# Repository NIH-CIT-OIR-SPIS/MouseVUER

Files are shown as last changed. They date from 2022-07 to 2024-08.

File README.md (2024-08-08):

# MouseVUER: Video based open-source system for laboratory mouse home-cage monitoring

### About

An open source home-cage design based on Intel&reg; RealSense&trade; depth cameras. 

### CAD Files and Assembly

The CAD files and assembly instructions can be found in the [CAD_Models folder](./CAD_Models/).

### Manuscript data

The images and annotations used in the manuscript can be found here [Manuscript_Data folder](./Manuscript_Data/)

# Video Acquisition Software

<p>
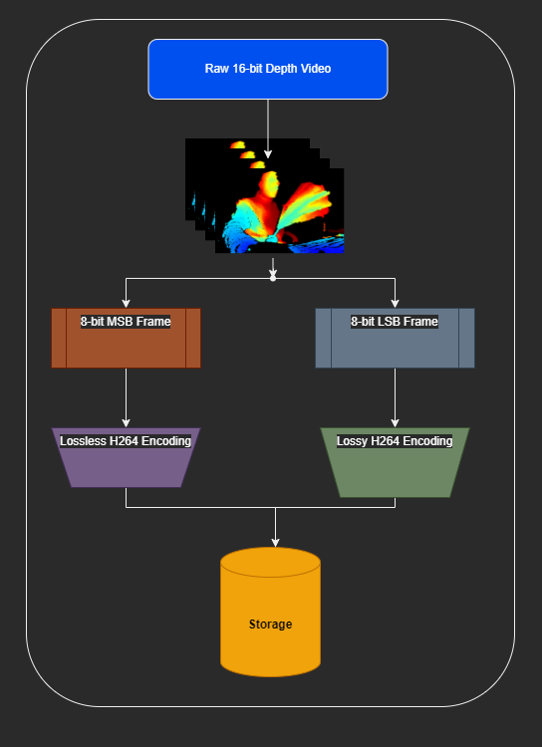
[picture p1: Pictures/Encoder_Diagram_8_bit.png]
    
    <br>
    <em>Depth Video Encoding Pipeline</em>
</p>

### Directions for Installation

### Install librealsense with Ubuntu 20.04 (as of 3/28/2023)

This is a guide on how to run the program 
To install with linux please follow directions here https://github.com/IntelRealSense/librealsense/blob/master/doc/distribution_linux.md

### Install python3 modules
```
sudo apt update && \
sudo apt install python3-pip && \
python3 -m pip install scapy && \
python3 -m pip install pycrypto && \
python3 -m pip install ffmpeg-python && \
python3 -m pip install numpy && \
sudo apt-get install python3-tk
```

### Install Boost, FFmpeg, GLFW3 and others using the following commands:

Type the following into the command line:
```
sudo apt-get -y install libboost-all-dev && \
sudo apt-get -y install libglfw3 && \
sudo apt-get -y install libglfw3-dev && \
sudo apt-get -y install freeglut3-dev libgl1-mesa-dev libglu1-mesa-dev  && \
sudo apt-get -y install libjsoncpp-dev && \
sudo apt-get -y install ffmpeg && \
sudo apt-get -y install libavcodec-dev libavutil-dev libavformat-dev libswscale-dev
```

### OPTIONAL Install Intel QuickSync
```
sudo apt install intel-media-va-driver-non-free x264 libva-dev libmfx-dev intel-media-va-driver-non-free x264 intel-media-va-driver-non-free i965-va-driver-shaders && \
export LIBVA_DRIVER_NAME=iHD
```
More info https://trac.ffmpeg.org/wiki/Hardware/VAAPI

### Install OpenCV with the following directions

https://linuxize.com/post/how-to-install-opencv-on-ubuntu-20-04/

## If the above doesn't work
from 
https://docs.opencv.org/4.6.0/d7/d9f/tutorial_linux_install.html
1) Install manually using guide below.
```
python3 -m pip install pyrealsense2 && \
sudo apt install -y g++ && \
sudo apt install -y cmake && \
sudo apt install -y make && \
sudo apt install -y wget unzip && \
sudo apt install -y git && \
cd ~/ && \
wget -O opencv.zip https://github.com/opencv/opencv/archive/4.x.zip && \
unzip opencv.zip && \
mv opencv-4.x opencv && \
mkdir -p build && cd build && \
cmake -DOPENCV_GENERATE_PKGCONFIG=ON ../opencv && \
make -j5 && \
sudo make install && \
sudo ldconfig -v
```

2) Then 

```
sudo nano /usr/local/lib/pkgconfig/opencv4.pc
```

3) And if nothing is there then copy the following to the opencv4.pc file please replace Version field with your specified version number :

```
# Package Information for pkg-config

prefix=/usr/local
exec_prefix=${prefix}
libdir=${exec_prefix}/lib
includedir=${prefix}/include/opencv4

Name: OpenCV
Description: Open Source Computer Vision Library
Version: 4.7.0 
Libs: -L${exec_prefix}/lib -lopencv_gapi -lopencv_highgui -lopencv_ml -lopencv_objdetect -lopencv_photo -lopencv_stitching -lopencv_video -lopencv_calib3d -lopencv_features2d -lopencv_dnn -lopencv_flann -lopencv_videoio -lopencv_imgcodecs -lopencv_imgproc -lopencv_core
Libs.private: -ldl -lm -lpthread -lrt
Cflags: -I${includedir}
```

4) Then do 
```
sudo nano ~/.bashrc
```

5) Now copy the following at the bottom of the .bashrc file
```
PKG_CONFIG_PATH=$PKG_CONFIG_PATH:/usr/local/lib/pkgconfig
export PKG_CONFIG_PATH
```

6) Now execute the command
```
sudo ldconfig -v
```

### Making your json file config
Connect your realsense camera and run
```
realsense-viewer
```

Then make any setting changes you wish to make and save changes using the save icon on the camera. You will be prompted to save it to a .json file
We will denote this json file as YourJsonFile.json

Save this file in the Code/ directory

### Directions for Use
Then plug in your Intel RealSense Camera into the computer's USB port

Then run:
```
cd ~/DepthCameraRecordingTool/Code/ && mkdir Testing_DIR
```

Then run:
```
make -j4
```

Or for a new run try
```
make clean && make -j4
```

Then in order to see a list of options do the following
```
./bin/multicam -h
```

### Examples
For example here is a simple recording for 30 seconds with files saved to Testing_DIR/

Decrease crf for better quality at expense of higher cpu processing and possible frame delays
thr just means number of cores you wish to utilize, default is 2, choose a number greater than 8 or 0 to cause it to use all cores
```
./bin/multicam -dir Testing_DIR/ -sec 30 -fps 30 -crf 23 -thr 0 -jsonfile Default.json
```

Record with depth, color and IR stream while aligning depth frames to color

```
./bin/multicam -dir Testing_DIR/ -sec 30 -fps 30 -crf 23 -thr 0 -jsonfile Default.json -color 1 -ir 1 -align_to_color 1
```

Record with just depth, and IR stream for 30 seconds 

```
./bin/multicam -dir Testing_DIR/ -sec 30 -fps 30 -crf 23 -thr 0 -jsonfile Default.json -ir 1
```

For command info  help type:

```
./bin/multicam -h
```

## Run multicam program

```
make -j4 && ./bin/multicam -sec 60 -thr 4 -fps 30 -crf 22 -numraw 450 -max_depth 1000 -dir Testing_DIR/ -bagfile ~/Downloads/fishy-fish.bag && ./bin/decompress Testing_DIR/test_lsb.mp4 Testing_DIR/test_msb.mp4 

```

### Decompress Lossy

Decompressing and comparing against raw files

```
./bin/decompress -ilsb Testing_DIR/test_lsb.mp4  -imsb Testing_DIR/test_msb.mp4 -hd Testing_DIR/video_head_file.txt -cmp Testing_DIR -o Testing_DIR -print_psnr 0
```

### Decompress Lossy

Decompressing regular no comparison

```
./bin/decompress -ilsb Testing_DIR/test_lsb.mp4  -imsb Testing_DIR/test_msb.mp4 -hd Testing_DIR/video_head_file.txt -o Testing_DIR -print_psnr 0
```

### Decompress each raw file seperately

```
ffmpeg -i Testing_DIR/test_lsb_5000_out.mp4 -i Testing_DIR/test_msb_5001_out.mp4 -map 0:v -c:v rawvideo -pix_fmt yuv420p Testing_DIR/output_lsb_5000.mkv -map 1:v -c:v rawvideo -pix_fmt yuv420p Testing_DIR/output_msb_5001.mkv
```

# Directions for Configuring Server Client System

### About

A server-client system for Depth Cameras.

<p>
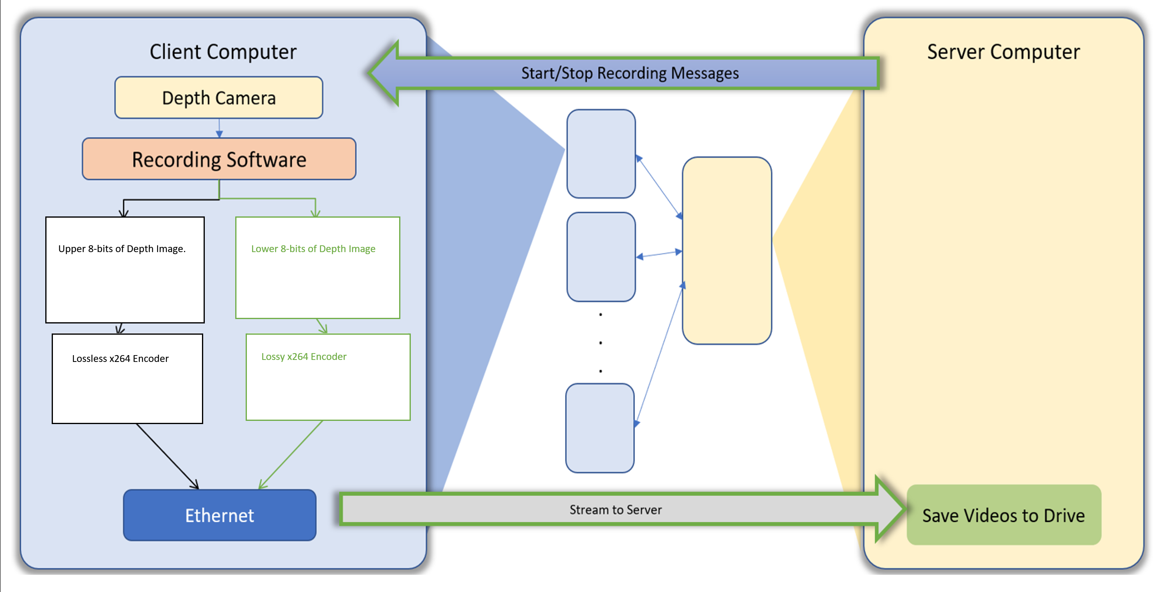
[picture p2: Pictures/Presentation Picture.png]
    
    <br>
    <em>Server-Client Configuration Diagram</em>
</p>
# Hardware Requirements.
Server computer should have more CPU cores for every client (Recommend for 3 or more systems should be at least 6th gen i5 desktop CPU or equivilant)

Client computers can be found for cheap if used (around $150 or less) for example (a used HP EliteDesk 800 G2 Mini Business Desktop with an i5-6500T is sufficiently powerful enough.)

Our configuration:
    Server (1):
        HP EliteDesk 800 G2 Mini Business Desktop with 16GB RAM and 5TB external drive
    
    Clients (multiple):
        HP EliteDesk 800 G2 Mini Business Desktop with 8GB RAM, and 128GB SSD     

Depth Cameras:
    Intel&reg; RealSense&trade; D435 Stereo Depth Cameras

Ubuntu 20.04 LTS is installed on each computer. See more configuration settings in the README.md document

## First please configure for static IP addresses:

### On server
Go to Settings -> Network -> Wired -> [Click on Settings Symbol] -> IPv4 -> Manual:

    Then enter the following into their respective boxes
    In Addresses section
        Address: 192.168.1.234
        Netmask: 255.255.255.0
        Gateway: 192.168.1.1
    In DNS section:
        8.8.4.4,8.8.8.8
    Then hit apply

**NOTE IF YOU HAVE ANY FIREWALL SETTINGS **

1) Open a terminal

2) Type in 

```
sudo ufw status verbose
```
3) You will see either an active status or inactive status

4) If you have an active status add rules so you can accept your client computer cameras

5) Type the following into a terminal 
```
sudo ufw allow proto tcp 192.168.1.201 to any port 5000 && sudo ufw allow proto tcp 192.168.1.201 to any port 5001 && \
sudo ufw allow proto tcp 192.168.1.202 to any port 5002 && sudo ufw allow proto tcp 192.168.1.202 to any port 5003 && \
sudo ufw allow proto tcp 192.168.1.203 to any port 5004 && sudo ufw allow proto tcp 192.168.1.202 to any port 5004 && \
.
.
.
...

```
If need be you can remove all the firewall rules by doing

```
sudo ufw status verbose
```

Looking at the number in the list at which the rule occurs at

```
sudo ufw delete [x] # Where x is the number in the list at which the rule occurs at which you want to delete
```
Key generation

Type the following in to a terminal on your Server

```
cd ~/DepthCameraRecordingTool/Code/ && \
make clean && make -j4 && \
python3 make_ssl_keys_cert.py
```

### On Client computers

Go to Settings -> Network -> Wired -> [Click on Settings Symbol] -> IPv4 -> Manual:
    Then enter the following into their respective boxes
    In Addresses section
        Address: 192.168.1.2xx    (Here xx means any two digit number as long as it is unique and not 34)
        Netmask: 255.255.255.0
        Gateway: 192.168.1.1
    In DNS section:
        8.8.4.4,8.8.8.8
    Then hit apply

### Copy Entire directory from Server to each client

Copy entire ~/DepthCameraRecordingTool/  directory to storage medium of your choice.
Then For ***each*** client computer:
    Navigate on the client computer to your home directory using the Files application on Ubuntu
    Paste a copy of the DepthCameraRecordingTool in this folder.

Alternativley you could just open up an ssh session to each client and copy the directories over. (This however assumes you are connecting the computers to routers)

### For each Client 
```
cd ~/DepthCameraRecordingTool/Code/ && \
make clean && \
make -j4
```

```
crontab -e
```
Then if prompted type in 1 and hit ENTER

Using the arrow keys go down to the very bottom of the file
Then add the following text replacing USER with your client username found if you go to settings and users:
```
@reboot sleep 10; export XAUTHORITY=/home/<USER>/.Xauthority; cd /home/<USER>/DepthCameraRecordingTool/Code/ && python3 client_side.py &
```
Then hit the keys CTRL+X then Y then ENTER

Then create a new bash script:
```
sudo nano /etc/NetworkManager/dispatcher.d/70-wifi-wired-exclusive.sh
```

Then copy and paste (Paste using the shortcut CTRL+SHIFT+V) the following into 70-wifi-wired-exclusive.sh:

```
#!/bin/bash
export LC_ALL=C

enable_disable_wifi ()
{
    result=$(nmcli dev | grep "ethernet" | grep -w "connected")
    if [ -n "$result" ]; then
        nmcli radio wifi off
    else
        nmcli radio wifi on
    fi
}

if [ "$2" = "up" ]; then
    enable_disable_wifi
fi

if [ "$2" = "down" ]; then
    enable_disable_wifi
fi
```
Then hit the keys CTRL+X then Y then ENTER

Then run the following command:
```
sudo chmod a+rx /etc/NetworkManager/dispatcher.d/70-wifi-wired-exclusive.sh
```

Then reboot the system
```
sudo reboot
```

Repeat for each client

## Running Server from CLI

Go to Settings -> Network -> Wired -> [Click on Settings Symbol] -> IPv4 -> Manual:
    Then enter the following into their respective boxes
    In Addresses section
        Address: 192.168.1.234
        Netmask: 255.255.255.0
        Gateway: 192.168.1.1
    In DNS section:
        8.8.4.4,8.8.8.8
    Then hit apply
    
Running a recording for 30 seconds at a crf of 22, with 4 clients connected
```
python3 server_side.py --dir Testing_DIR/ --num_clients 4 --json Default.json --time_run 30 --crf 22
```

## Running Server from GUI

Run the following command in mousePad/Code directory
```
python3 server_gui.py 
```

You should then see an image like this:

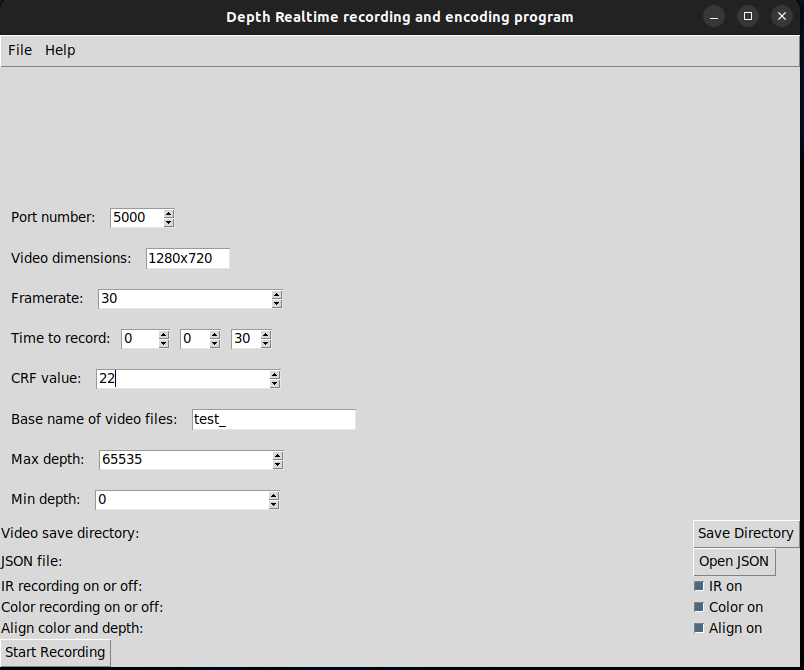
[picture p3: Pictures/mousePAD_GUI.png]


CRF values control the quality of the video. The higher the CRF value the lower the quality. Please keep it between 18-28.

Valid video dimensions are 640x480, and 1280x720

Please Choose a valid JSON to utilize.

You could also enter in your own json file as well for different settings just be sure that these files are also on the client computers.

# Directions Collecting_Training_Code/

### Running recording lossless compression with GUI

```
cd ~/DepthCameraRecordingTool/Code/Collect_Training_Code/
python3 collect_aligned_depth_training_vids.py
```

### Decompressing each frame to a TIF file GUI

```
python3 decompress_training_vids_gui.py
```

### Run collect_raw for 30 seconds using ffv1, with aligned frames from directory Collect_Training_Code/

make -j4 && ./bin/collect_raw -dir Testing_DIR/ -sec 30 -align 1 -jsonfile ../Code/Default.json

# Other Helpful Commands for Developers
To look at frame rates

```
ffprobe Testing_DIR/test_lossy.h265 -count_frames -show_entries stream=nb_read_frames,avg_frame_rate,r_frame_rate
```

To look at stats of a video please see the following from (https://ffmpeg.org/ffprobe-all.html)

```
ffprobe -f lavfi movie=Testing_DIR/test_lsb.mp4,signalstats -show_entries frame_tags=lavfi.signalstats.YMAX,lavfi.signalstats.YMIN,lavfi.signalstats.YAVG,lavfi.signalstats.YBITDEPTH,lavfi.signalstats.YDIF
```
Automate GDB

```
for i in {1..20}; do gdb -q -ex 'set pagination off' -ex 'set args -dir Testing_DIR/ -sec 15 -numraw 450 -crf 17 -bagfile ~/Downloads/One_Mouse_5_minutes_depth.bag' -ex run  ./bin/multicam -ex quit; done
```

Play videos side by side ffplay

```
ffplay -f lavfi "movie=left.mp4,scale=iw/2:ih[v0];movie=right.mp4,scale=iw/2:ih[v1];[v0][v1]hstack"
```

See info ffmpeg
```
ffmpeg -h encoder=libx264
```

## Utility Functions found in ~/DepthCameraRecordingTool/Code/util_functions
```
python3 decompress_from_bag_file.py -f test.bag -o Testing_DIR/
```

From depth coordinates (feeding in depth frame as png or tif) to xyz world coordinates given a set of points on the image plane in this example I am using 3 coordinates, you can use any number of coordinates, 
```
python3 from_depth_to_xyz.py -cal ../Testing_DIR/intrinsics.json -d Testing_DIR2/depth/depth_frm_40.tif -l "(13,20),(13,30),(640, 360)"
```

```
python3 script_sort_depth.py -f /media/<username>/DRIVE/images -f2 /media/<username>/DRIVE/out\(Gouda\)/
```

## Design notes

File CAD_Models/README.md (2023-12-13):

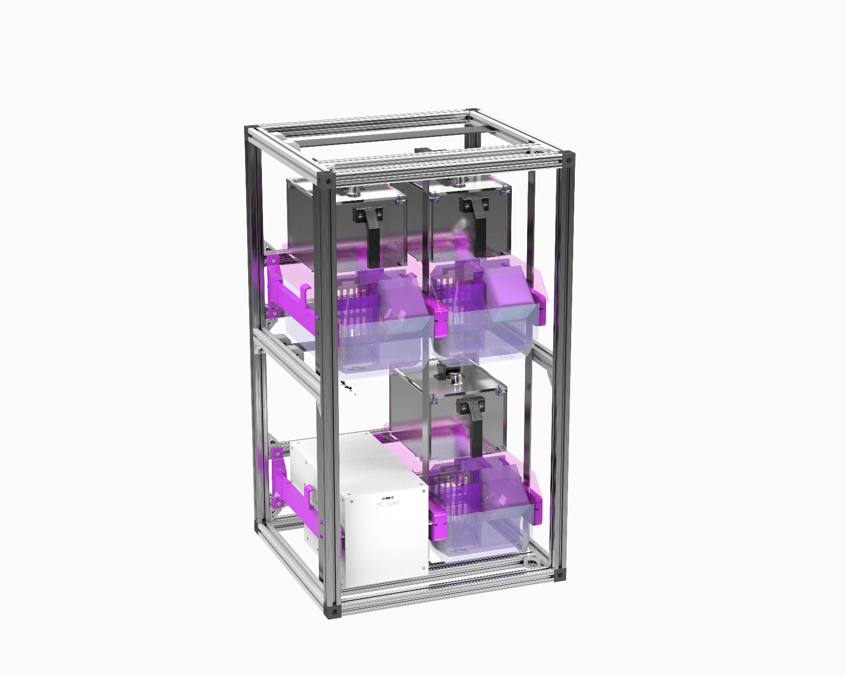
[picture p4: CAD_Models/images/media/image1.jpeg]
{width="4.468751093613299in"
height="6.0in"}

# Table of Contents {#table-of-contents .TOC-Heading}

[MouseVUER System Overview
[4](#mousevuer-system-overview)](#mousevuer-system-overview)

[The Monitoring Cage Assembly
[4](#the-monitoring-cage-assembly)](#the-monitoring-cage-assembly)

[The Monitoring Cage Overview
[4](#the-monitoring-cage-overview)](#the-monitoring-cage-overview)

[Monitoring Cage Unit Fabrication
[5](#monitoring-cage-unit-fabrication)](#monitoring-cage-unit-fabrication)

[Modified Lid Fabrication
[5](#modified-lid-fabrication)](#modified-lid-fabrication)

[Hopper Fabrication [5](#hopper-fabrication)](#hopper-fabrication)

[Camera Mounting Enclosure Fabrication [5](#camera-mounting-enclosure-fabrication)](#camera-mounting-enclosure-fabrication)

[Monitoring Cage Assembly
[6](#monitoring-cage-assembly)](#monitoring-cage-assembly)

[Hopper Assembly [7](#hopper-assembly)](#hopper-assembly)

[Camera Mounting Enclosure Assembly [8](#camera-mounting-enclosure-assembly)](#camera-mounting-enclosure-assembly)

[Finished Monitoring Cage Unit Assembly
[10](#finished-monitoring-cage-unit-assembly)](#finished-monitoring-cage-unit-assembly)

[The Power and Control Module (PCM) Assembly
[12](#the-power-and-control-module-pcm-assembly)](#the-power-and-control-module-pcm-assembly)

[PCM Overview [12](#pcm-overview)](#pcm-overview)

[System Fabrication [12](#system-fabrication)](#system-fabrication)

[Enclosure Fabrication
[13](#enclosure-fabrication)](#enclosure-fabrication)

[The PCM Assembly [13](#the-pcm-assembly)](#the-pcm-assembly)

[Side and Top Panel Assemblies
[16](#side-and-top-panel-assemblies)](#side-and-top-panel-assemblies)

[Electronic Subassemblies
[17](#electronic-subassemblies)](#electronic-subassemblies)

[Main Body Assembly [19](#main-body-assembly)](#main-body-assembly)

[Modular Rack Assembly
[23](#modular-rack-assembly)](#modular-rack-assembly)

[Modular Rack Overview
[23](#modular-rack-overview)](#modular-rack-overview)

[Modular Rack Fabrication
[23](#modular-rack-fabrication)](#modular-rack-fabrication)

[Modular Rack Assembly
[23](#modular-rack-assembly-1)](#modular-rack-assembly-1)

[Appendix -- Step by Step Instructions
[35](#appendix-step-by-step-instructions)](#appendix-step-by-step-instructions)

[Monitoring Cage Assembly
[35](#monitoring-cage-assembly-1)](#monitoring-cage-assembly-1)

[Hopper Assembly [35](#hopper-assembly-1)](#hopper-assembly-1)

[Camera Mounting Enclosure Assembly [37](#camera-mounting-enclosure-assembly-1)](#cme-assembly-1)

[Monitoring Cage Unit Assembly
[42](#monitoring-cage-unit-assembly)](#monitoring-cage-unit-assembly)

[Power and Control Module (PCM)
[44](#power-and-control-module-pcm)](#power-and-control-module-pcm)

[Side Panel Subassembly [44](#_Toc147213275)](#_Toc147213275)

[Top Panel Subassembly
[48](#top-panel-subassembly)](#top-panel-subassembly)

[Power Supply Subassembly
[49](#power-supply-subassembly)](#power-supply-subassembly)

[Power Distribution Board Subassembly
[50](#power-distribution-board-subassembly)](#power-distribution-board-subassembly)

[SBC Subassembly [51](#sbc-subassembly)](#sbc-subassembly)

[PCM Main Body Assembly
[53](#pcm-main-body-assembly)](#pcm-main-body-assembly)

[Modular Rack Assembly
[65](#modular-rack-assembly-2)](#modular-rack-assembly-2)

[Rack Top Subassembly
[65](#rack-top-subassembly-1)](#rack-top-subassembly-1)

[Rack Base Subassembly
[70](#rack-base-subassembly-1)](#rack-base-subassembly-1)

[Rack Mid Bar Subassembly
[74](#rack-mid-bar-subassembly-1)](#rack-mid-bar-subassembly-1)

[Rack Rear Bar Subassembly
[76](#rack-rear-bar-subassembly-1)](#rack-rear-bar-subassembly-1)

[Rack Assembly [78](#rack-assembly-1)](#rack-assembly-1)

# 

# MouseVUER System Overview

The Mouse Video Utility for Experiments Recording (MouseVUER) is an
open-source system for housing and monitoring rodents for experiments.
The MouseVUER system fits inside a custom modular rack that houses all
the components for running the system. The monitoring cage units are
where the rodents are monitored. There are three monitoring cage units
per MouseVUER system. Each monitoring unit has subassemblies including
a Camera Mounting Enclosure and Hopper that must be assembled. The camera mounting enclosure supports the
camera and LEDs above the mouse lid. The hopper is specially designed to
fit into the mouse cages and supply food and water. One Power and
Control Module (PCM) will need to be fabricated for every MouseVUER
system. The PCM is responsible for powering and housing electronics to
run the MouseVUER system. Figure 1 shows the components of the MouseVUER
system.

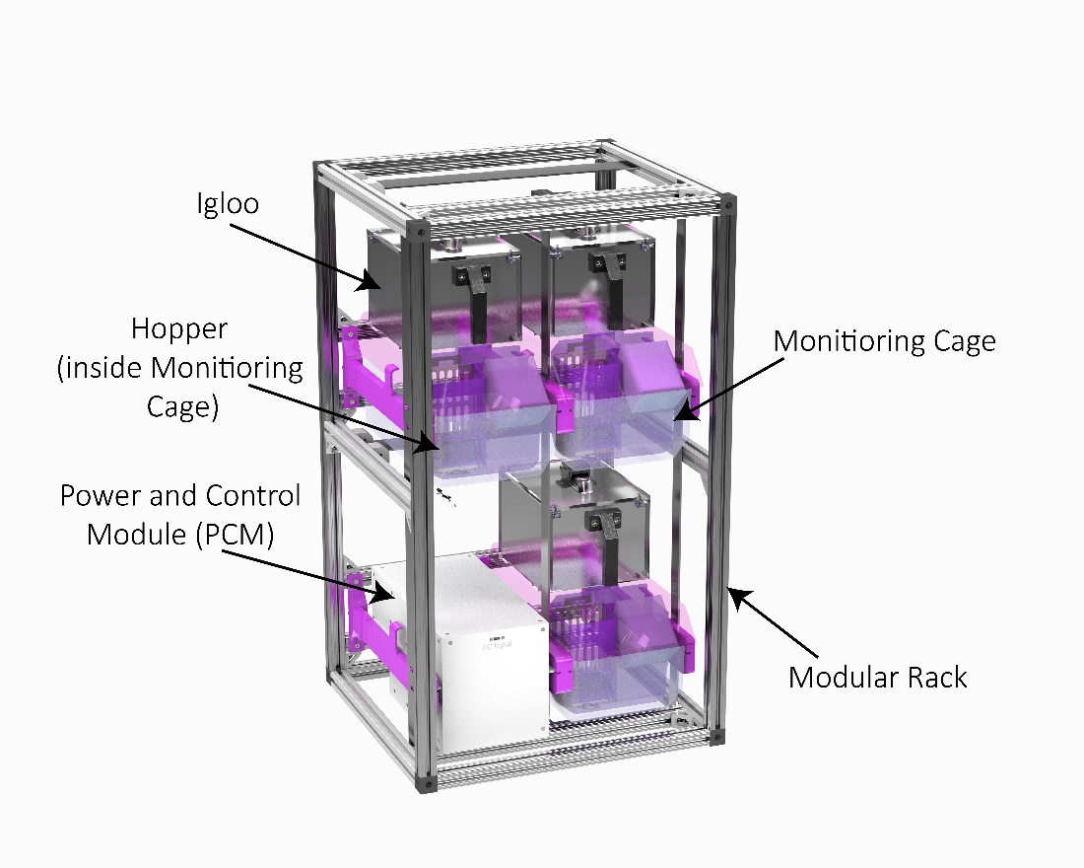
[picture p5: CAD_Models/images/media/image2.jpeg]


Figure 1 Fully assembled MouseVUER system.

This document is organized into subassemblies to build the final
MouseVUER system. Each subassembly has a fabrication and assembly
section. Each subassembly has a bill of materials for one subassembly
unit. In the appendix, larger figures of all assembly steps are shown.

# The Monitoring Cage Assembly

## The Monitoring Cage Overview

The Monitoring Cage units are where the rodents are monitored. These
instructions are for one Monitoring Cage unit and must be repeated two
more times for each MouseVUER system. The Monitoring Cage unit has
subassemblies called the Camera Mounting Enclosure and Hopper that must be assembled before
assembling the final Monitoring Cage unit.

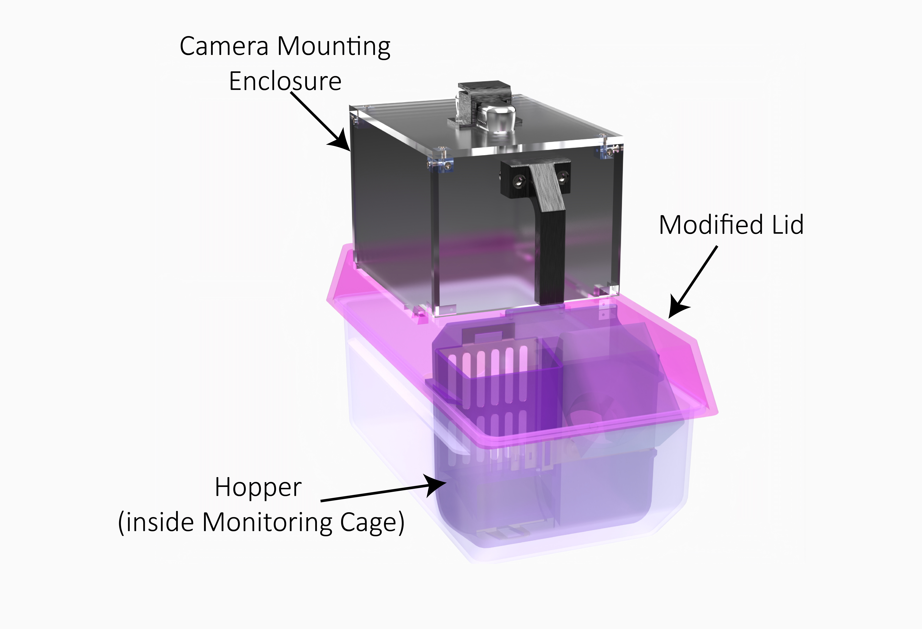
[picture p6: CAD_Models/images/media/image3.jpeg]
{width="5.865580708661417in"
height="4.0in"}

Figure 2 The final Monitoring Cage unit Assembly

## Monitoring Cage Unit Fabrication

### Modified Lid Fabrication

A solid clear NexGen lid (P/N: 228790-1, Allentown Inc, Allentown, NJ)
will need to be modified to support the Monitoring Cage unit. A DXF file
can be found on the Github page, and it will need to cut into the lid.
In this fabrication process, a waterjet was used to make the cuts into
the lid. In this process, a single pass of the waterjet was used even
for the varying heights of the lid.

### Hopper Fabrication

The two-compartment hopper was designed to house food pellets and a
water bottle inside the NexGen standard cage (P/N: 223581-4, Allentown
Inc, Allentown, NJ). The hopper must be injection molded (ICOMold Inc.,
Hartland, WI) from a food safe, autoclavable material (PSU Ultrason
S3010, BASF, Ludwigshafen, Germany). The food grate (304SS, 26-gauge,
Yarde Metal, White Marsh, MD) is fabricated with a waterjet and bending
tool. The bottle holder (304SS, 24-gauge, Yarde Metal, White Marsh, MD)
is fabricated with a waterjet.

### Camera Mounting Enclosure Fabrication

The camera mounting enclosure consists of five clear acrylic panels fixed together to
support a camera above the mouse cage. The acrylic panels (Clear Cast
Acrylic-1/4", Piedmont Plastics, Elkridge, Maryland) must be cut. In
this fabrication process a CO~2~ laser cutter (PLS6.150D, Universal
Laser Systems) was used for cutting the panels. Holes on the panels will
need to be countersink with a 90° Countersink drill bit. Two holes on
the top panel will need to be tapped for 4-40 threads. The handle and
camera bracket will need to be 3D printed. In this fabrication process,
the Markforged X7 (Waltham, MA) was used to print the parts out of Onyx.

## Monitoring Cage Assembly

The bill of materials for the assembly of one Monitoring Cage unit is
shown in Table 1. The mouse cage lid must be modified before assembling
the Monitiroing Cage unit. Items that were custom made have .STP or .DXF
or .STL files to reference on the Github page. All other items were
purchased from vendors.

<table>
<caption><p>Bill of materials for the assembly of one MouseVUER
unit.</p></caption>
<colgroup>
<col style="width: 7%" />
<col style="width: 15%" />
<col style="width: 22%" />
<col style="width: 14%" />
<col style="width: 17%" />
<col style="width: 8%" />
<col style="width: 14%" />
</colgroup>
<tbody>
<tr class="odd">
<td>ITEM NO.</td>
<td>Part Label</td>
<td>Description</td>
<td>Source</td>
<td>Vendor Part Number</td>
<td>Qty</td>
<td>Cost</td>
</tr>
<tr class="even">
<td>1</td>
<td>Mouse Cage Base</td>
<td>MOUSE, XJ/NEXGEN, CLEAR POLYSULFONE HIGH TEMPERATURE PLASTIC, WHITE
AIR KUP</td>
<td>Allentown Inc.</td>
<td>223581-4</td>
<td>1</td>
<td>$48.60</td>
</tr>
<tr class="odd">
<td>2</td>
<td>Mouse Cage Lid</td>
<td>MICRO BARRIER TOP, MOUSE, NEXGEN, SOLID, CLEAR POLYSULFONE HIGH
TEMPERATURE PLASTIC, NO LOCKS</td>
<td>Allentown Inc.</td>
<td>228790-1</td>
<td>1</td>
<td>$139.50</td>
</tr>
<tr class="even">
<td>3</td>
<td>Water bottle</td>
<td> Bottle Udel 9 oz., Ink with "O" Ring</td>
<td>Thoren Caging Systems, Inc.</td>
<td>BW09UIRNO</td>
<td>1</td>
<td>$7.11</td>
</tr>
<tr class="odd">
<td>4</td>
<td>Sipper Tube</td>
<td>Stainless steel with 2 1/2" welded bent sipper tube</td>
<td>Thoren Caging Systems, Inc.</td>
<td>BWCS250HSB</td>
<td>1</td>
<td>$3.79</td>
</tr>
<tr class="even">
<td>5</td>
<td>Hopper</td>
<td>PSU Ultrason S3010</td>
<td>Injection Molded</td>
<td>N/A - refer to STP file</td>
<td>1</td>
<td>$92.19</td>
</tr>
<tr class="odd">
<td>6</td>
<td>Stainless Steel Grommet</td>
<td>Stainless Steel Fabric Grommets with Washer</td>
<td>McMaster-Carr</td>
<td>96015K33</td>
<td>1</td>
<td>$16.68</td>
</tr>
<tr class="even">
<td>7</td>
<td>Food Grate</td>
<td>304SS, 26 Gauge stock piece</td>
<td>Waterjet Cut</td>
<td>N/A - refer to DXF file</td>
<td>1</td>
<td></td>
</tr>
<tr class="odd">
<td>8</td>
<td>Bottle Holder</td>
<td>304SS, 24 Gauge stock piece</td>
<td>Waterjet Cut</td>
<td>N/A - refer to DXF file</td>
<td>1</td>
<td></td>
</tr>
<tr class="even">
<td>9</td>
<td>4-40, 3/8" Flat</td>
<td>Passivated 18-8 Stainless Steel Phillips Flat Head Screw</td>
<td>McMaster-Carr</td>
<td>91099A165</td>
<td>2</td>
<td>$5.55</td>
</tr>
<tr class="odd">
<td>10</td>
<td>Camera</td>
<td>Depth Camera D435</td>
<td>Intel Inc.</td>
<td>D435</td>
<td>1</td>
<td>$314.00</td>
</tr>
<tr class="even">
<td>11</td>
<td>Camera Bracket</td>
<td>3D Printed FDM</td>
<td>3D printed</td>
<td>N/A - refer to STL file</td>
<td>1</td>
<td>$3.00</td>
</tr>
<tr class="odd">
<td>12</td>
<td>1/4"-20, 3/8" Flat</td>
<td>Passivated 18-8 Stainless Steel Phillips Flat Head Screw</td>
<td>McMaster-Carr</td>
<td>91771A535</td>
<td>1</td>
<td>$12.13</td>
</tr>
<tr class="even">
<td>13</td>
<td>1/4"-20 Nut</td>
<td>18-8 Stainless Steel Thin Hex Nut</td>
<td>McMaster-Carr</td>
<td>91847A029</td>
<td>2</td>
<td>$6.36</td>
</tr>
<tr class="odd">
<td>14</td>
<td>1/4"-20, 7/8" Flat</td>
<td>Passivated 18-8 Stainless Steel Phillips Flat Head Screw</td>
<td>McMaster-Carr</td>
<td>91099A478</td>
<td>2</td>
<td>$12.99</td>
</tr>
<tr class="even">
<td>15</td>
<td>Handle</td>
<td>3D Printed FDM</td>
<td>3D printed</td>
<td>N/A - refer to STL file</td>
<td>1</td>
<td>$10.00</td>
</tr>
<tr class="odd">
<td>16</td>
<td>M3, 10mm Flat</td>
<td>316 Stainless Steel Phillips Flat Head Screw</td>
<td>McMaster-Carr</td>
<td>91801A156</td>
<td>12</td>
<td>$9.91</td>
</tr>
<tr class="even">
<td>17</td>
<td>Camera Mounting Enclosure Front Panel</td>
<td>Cut from 12"x24"x1/4" Clear Cast Acrylic</td>
<td>Laser Cut</td>
<td>N/A - refer to DXF file</td>
<td>1</td>
<td>$13.00</td>
</tr>
<tr class="odd">
<td>18</td>
<td>Camera Mounting Enclosure Side Panel</td>
<td>Cut from 12"x24"x1/4" Clear Cast Acrylic</td>
<td>Laser Cut</td>
<td>N/A - refer to DXF file</td>
<td>2</td>
<td>$13.00</td>
</tr>
<tr class="even">
<td>19</td>
<td>Camera Mounting Enclosure Top Panel</td>
<td>Cut from 12"x24"x1/4" Clear Cast Acrylic</td>
<td>Laser Cut</td>
<td>N/A - refer to DXF file</td>
<td>1</td>
<td>$13.00</td>
</tr>
<tr class="odd">
<td>20</td>
<td>Cube Standoff</td>
<td>Aluminum M3 Modding Cubes</td>
<td>V1 Tech</td>
<td>N/A</td>
<td>4</td>
<td>$5.00</td>
</tr>
<tr class="even">
<td colspan="6">Total Cost Per MouseVUER Unit</td>
<td>$725.81</td>
</tr>
</tbody>
</table>

### Hopper Assembly 

The hopper subassembly should be completed before inserting into the
Monitoring Cage unit. The first step involves using a hammer-driven
punch (9612K28, McMaster-Carr, Elmhurst, IL) to lock the stainless steel
grommet in place. The food grate is then inserted and locked in by two
tabs. Lastly, the bottle holder is inserted and locked in via tabs. The
hopper assembly instructions are shown in Figure 3.

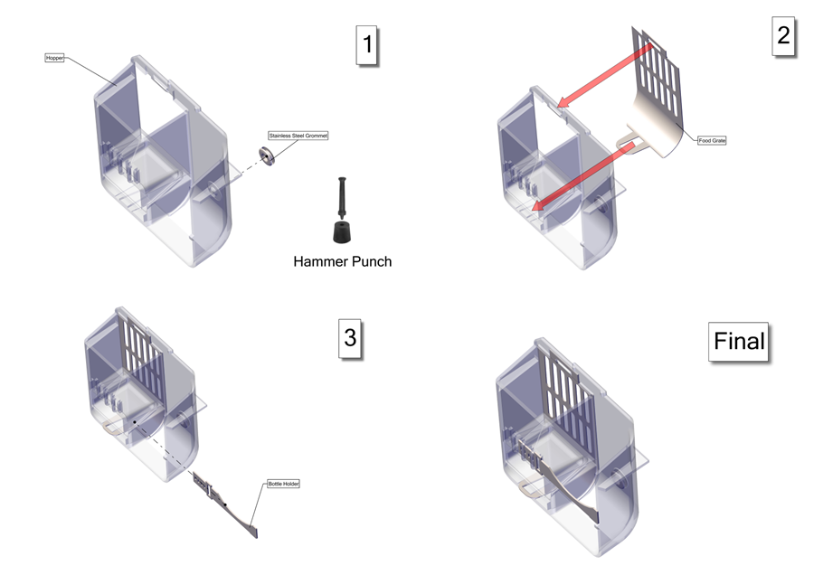
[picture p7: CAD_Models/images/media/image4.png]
{width="6.000694444444444in"
height="4.240277777777778in"}

Figure 3 The Hopper sub assembly.

### Camera Mounting Enclosure Assembly 

The Camera Mounting Enclosure subassembly must be completed before inserting into the
Monitoring Cage unit. A Phillips no. 2 screwdriver will be required for
fastening all screws in this section. The first four steps in the Camera Mounting Enclosure
assembly are shown in Figure 4. Four cube standoffs will be fastened to
the top panel with four M3, 10mm flat screws. The rear panel will be
secured via two M3, 10mm flat screws. Next, the 2 side panels will be
secured by two M3, 10mm flat screws for each panel.

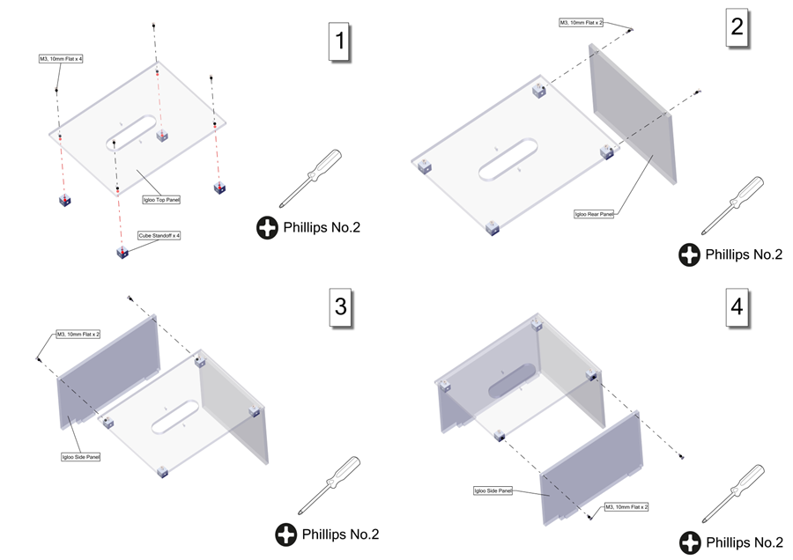
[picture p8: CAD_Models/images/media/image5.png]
{width="5.660661636045495in"
height="4.0in"}

Figure 4 Steps 1 to 4 of the Camera Mounting Enclosure subassembly.

The next step is to fasten the front panel with two M3, 10mm flat
screws. The handle will be secured in place via two ¼"-20, 7/8" flat
screws and two ¼"-20 nuts. The camera is bolted to the camera bracket by
a ¼"-20, 3/8" flat screw. Two 4-40, 3/8" screws are used to fasten the
camera bracket to the Camera Mounting Enclosure. These steps are shown in Figure 5. The
final Camera Mounting Enclosure subassembly is shown in Figure 6.

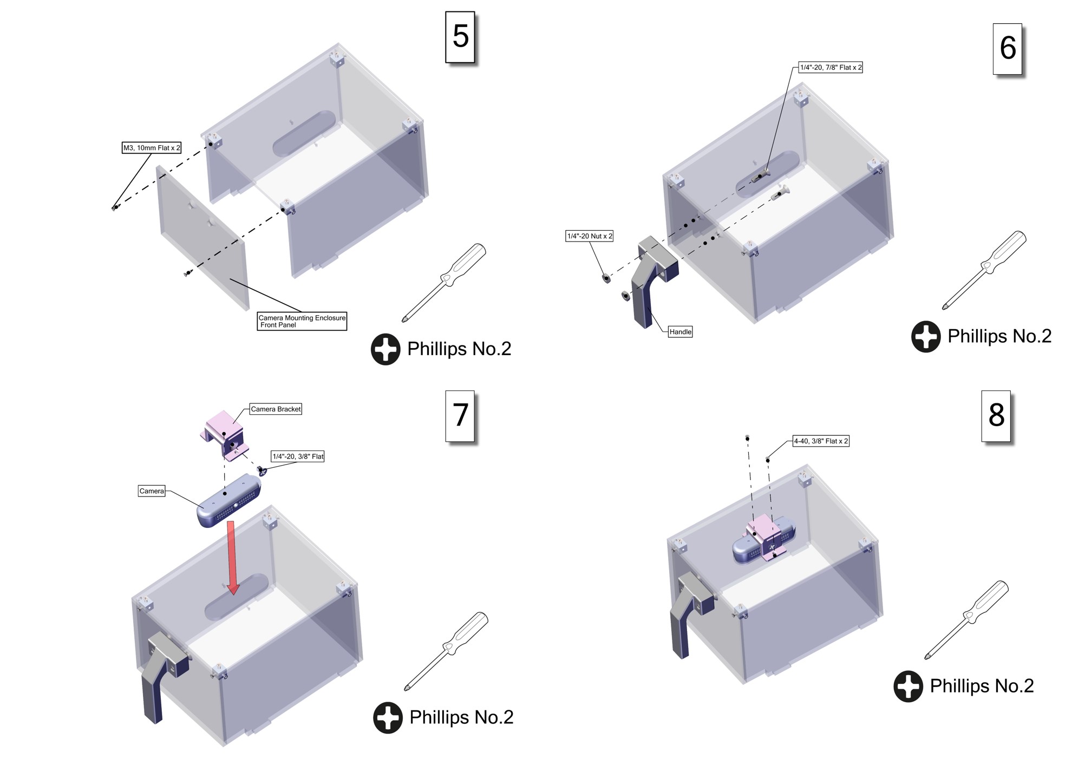
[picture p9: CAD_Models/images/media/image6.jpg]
{width="5.660661636045495in"
height="4.0in"}

Figure 5 Steps 5 to 8 for the Camera Mounting Enclosure subassembly.

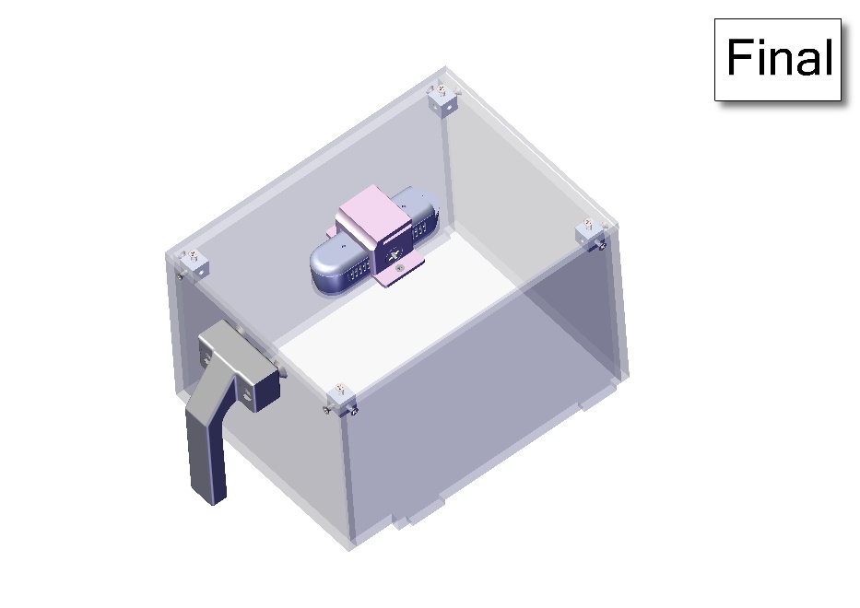
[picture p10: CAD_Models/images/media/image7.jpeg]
{width="4.24297353455818in"
height="3.0in"}

Figure 6 The final Camera Mounting Enclosure subassembly.

### Finished Monitoring Cage Unit Assembly 

Once the hopper and camera mounting enclosure assemblies are completed, the Monitoring Cage
unit can be constructed. Four steps are required in this process, and
they are shown in Figure 7. The first step is to insert the hopper near
the front of the mouse cage base. Next, the water bottle is inserted
into the hopper. The third step involves securing the hopper in place
via a tab on the mouse cage lid. The blue arrow in step 3 shows the
locking tab. The last step is to insert the camera mounting enclosure to the mouse cage lid
by aligning the four cutouts shown via 4 red arrows. The final
Monitoring Cage assembly is shown in Figure 8.

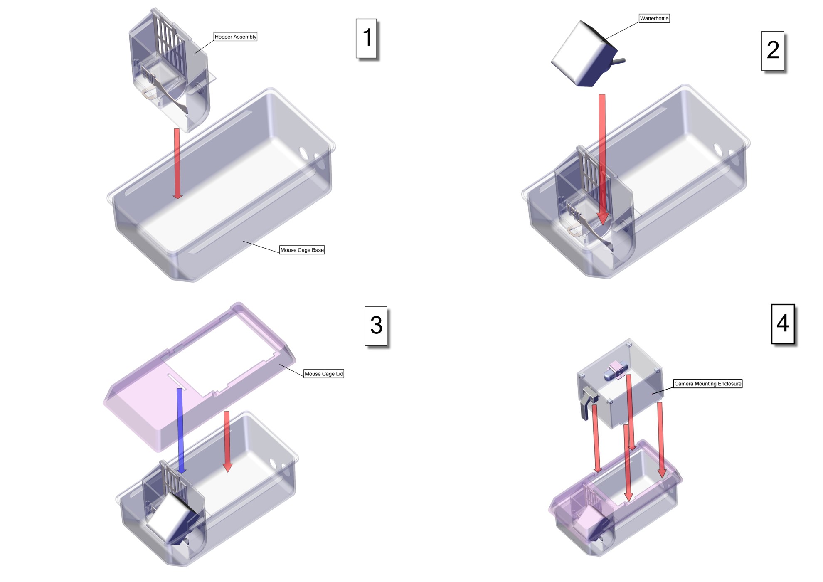
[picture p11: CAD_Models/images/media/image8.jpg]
{width="5.660661636045495in"
height="4.0in"}

Figure 7 The steps to complete the Monitoring Cage assembly.

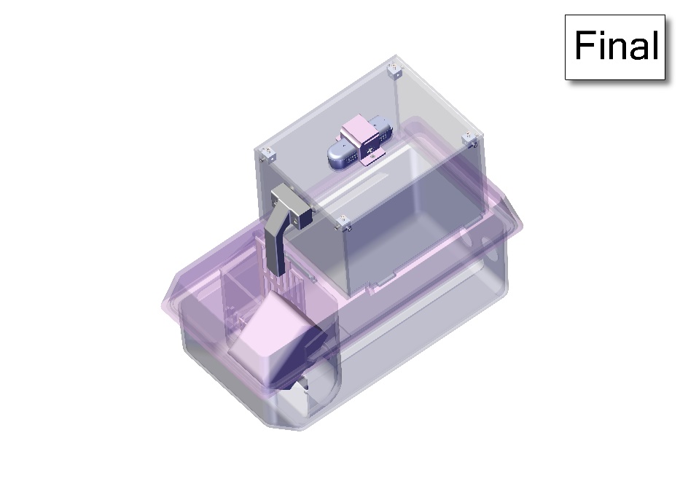
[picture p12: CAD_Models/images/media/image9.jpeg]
{width="4.24297353455818in"
height="3.0in"}

Figure 8 The final Monitoring Cage assembly.

# The Power and Control Module (PCM) Assembly

## PCM Overview

The PCM is responsible for powering, controlling, and data communication
with three Monitoring Cage units to successfully monitor the rodents.
The PCM is designed to slide into one of the open slots on the custom
racks using 3D printed rails. The PCM will have electronic connections
in the rear to the three Monitoring Cage units. Each PCM has three
single board computers (SBC) (70878-AI-TX2, Auvidea Denklingen, Germany)
utilized as compression units compressing data from one of the
Monitoring Cage units and sends the data via ethernet to the network
switch (EH2306, ATOP Technologies, Zhubei City, Taiwan) inside the PCM.
The switch relays the data to an ethernet panel mount (MRJ-5780-01,
Amphenol ICC, Wallingford, CT) on the PCM that can be sent to an
external storage system for the user. The PCM has a power supply
(MPB125-4350G, Bel Power Solutions, New Jersey City, NJ) that connects
to a power entry module (KM01.1105.11, Schurter Inc., Santa Rosa, CA)
which can be powered to a standard AC 110V wall outlet. The power supply
is connected to a custom power distribution board responsible for
powering the internal components of the PCM. The internal components
powered by the power distribution board include the three SBC
compression units, the ethernet switch, a fan (MF40100V1-1000U-A99,
Sunon Fans, Brea, CA) and a microcontroller (2590, Adafruit Industries
LLC, New York, NY). The fan helps with thermal management by providing
airflow through the PCM to prevent overheating of the internal
components. The microcontroller allows for controlling auxiliary power
options. The PCM has multiple connections in the rear as shown in figure
2. Two connections are for the power module and ethernet port. Three
connections are for individual data communication between the PCM and
each Monitoring Cage unit. Three 6 pin connectors are available for
auxiliary power for future abilities such as controlling LED lighting on
each of the Monitoring Cage units.

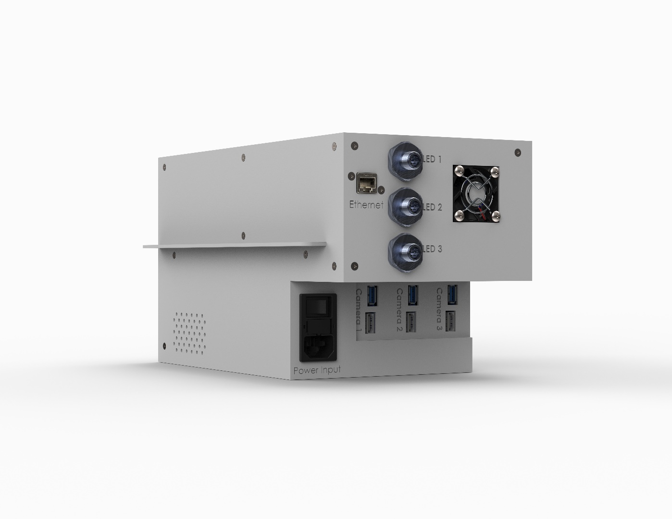
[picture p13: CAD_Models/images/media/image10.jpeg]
A picture containing electronics, camera Description automatically generated
{width="4.442297681539808in"
height="3.1333333333333333in"}

Figure 9 The PCM backside with electrical connections and fan.

## System Fabrication 

The PCM was designed using 3D computer-aided design (CAD) software
SolidWorks 2022 (Dassault Systems SolidWorks Corporation, Concord, NH).
ABS material components were printed using a FDM printer (F370,
Stratasys, Rehovot, Israel). Cast acrylic components were cut from bulk
material using a CO~2~ laser cutter (PLS6.150D, Universal Laser Systems,
Scottsdale, AZ).

## Enclosure Fabrication

The enclosure consists of four parts: the main body, rail, top panel,
and right panel. The top and right panels were fabricated by cutting
them out of 12"x24"x1/8" cast acrylic using a laser cutter. Afterwards
countersinks were drilled into the holes using a 90° Countersink drill
bit. The main body and rail were 3D printed using a FDM 3D printer and
GrabCAD Print software from Stratasys. The print orientation for the
parts at 0.0130-inch slice height is shown in figure 10.

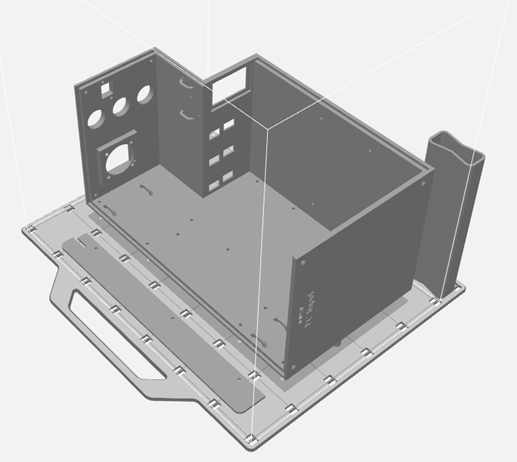
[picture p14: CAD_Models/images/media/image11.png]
{width="2.632782152230971in"
height="2.352742782152231in"}

Figure 10 Main body and rail orientation for 3D printing in GrabCAD
Print.

## The PCM Assembly

The bill of materials for the assembly of the PCM is shown in Table 2.
The main body, rail, top panel, and side panel must be fabricated as
previously mentioned. The power distribution board must also be
fabricated. In this design, the power distribution board was designed in
Altium Designer (Altium, San Diego, CA) and fabricated using a circuit
board plotter (LPKF S104, LPKF Laser & Electronics, Garbsen, Germany).
Items that were custom made have .DXF or .STL files to reference on the
Github page. The other items were purchased from vendors.

<table>
<caption><p>Bill of materials for the Control Center
assembly.</p></caption>
<colgroup>
<col style="width: 7%" />
<col style="width: 15%" />
<col style="width: 22%" />
<col style="width: 14%" />
<col style="width: 17%" />
<col style="width: 8%" />
<col style="width: 14%" />
</colgroup>
<thead>
<tr class="header">
<th>ITEM NO.</th>
<th>Part Label</th>
<th>Description</th>
<th>Source</th>
<th>Vendor Part Number</th>
<th>Qty</th>
<th>Cost</th>
</tr>
</thead>
<tbody>
<tr class="odd">
<td>1</td>
<td>Main Body</td>
<td>3D Printed FDM</td>
<td>N/A</td>
<td>N/A – refer to STL file</td>
<td>1</td>
<td>$150.00</td>
</tr>
<tr class="even">
<td>9</td>
<td>Rail</td>
<td>3D Printed FDM</td>
<td>N/A</td>
<td>N/A – refer to STL file</td>
<td>1</td>
<td>$3.00</td>
</tr>
<tr class="odd">
<td>10</td>
<td>Top Panel</td>
<td>Cut from 12"x24"x1/8" Cast Acrylic</td>
<td>Laser Cut</td>
<td>N/A – refer to DXF file</td>
<td>1</td>
<td>$13.00</td>
</tr>
<tr class="even">
<td>11</td>
<td>Side Panel</td>
<td>Cut from 12"x24"x1/8" Cast Acrylic</td>
<td>Laser Cut</td>
<td>N/A – refer to DXF file</td>
<td>1</td>
<td>$13.00</td>
</tr>
<tr class="odd">
<td>12</td>
<td>Power Distribution Board</td>
<td>LPKF Fabrication</td>
<td>N/A</td>
<td>N/A – refer to zip file</td>
<td>1</td>
<td>$125.00</td>
</tr>
<tr class="even">
<td>14</td>
<td>SBC Unit</td>
<td>JN30D for NVIDIA® Jetson Nano™ and TX2 NX™</td>
<td>Auvidea</td>
<td>70878-AI-TX2</td>
<td>3</td>
<td>$825.00</td>
</tr>
<tr class="odd">
<td>17</td>
<td>Power Supply</td>
<td>Open Frame AC DC Converters 4 Output 3.3V 5V 12V -12V 90 ~ 264 VAC
Input</td>
<td>Bel Power Solutions</td>
<td>MPB125-4350G</td>
<td>1</td>
<td>$169.00</td>
</tr>
<tr class="even">
<td>18</td>
<td>Switch</td>
<td>Network Switch-Unmanaged 6 Port</td>
<td>ATOP Technologies</td>
<td>EH2306</td>
<td>1</td>
<td>$113.00</td>
</tr>
<tr class="odd">
<td>19</td>
<td>Power Mount</td>
<td>PWR Entry Connector Receptacle, Male Blades - Module IEC 320-C14
Panel Mount, Snap-In</td>
<td>Schurter Inc.</td>
<td>KM01.1105.11</td>
<td>1</td>
<td>$15.95</td>
</tr>
<tr class="even">
<td>20</td>
<td>Ethernet Mount</td>
<td>CONN MOD Coupler 8P8C to 8P8C</td>
<td>Amphenol ICC (Commercial Products)</td>
<td>MRJ-5780-01</td>
<td>1</td>
<td>$21.84</td>
</tr>
<tr class="odd">
<td>21</td>
<td>USB Mount</td>
<td>CBL USB2.0 MCMR RCPT-MCR B Plug</td>
<td>Adafruit Industries LLC</td>
<td>3258</td>
<td>1</td>
<td>$4.95</td>
</tr>
<tr class="even">
<td>23</td>
<td>Fan</td>
<td>Fan Axial 40x10mm VAPO 5VDC Wire</td>
<td>Sunon Fans</td>
<td>MF40100V1-1000U-A99</td>
<td>1</td>
<td>$4.81</td>
</tr>
<tr class="odd">
<td>24</td>
<td>Fan Cover</td>
<td>Fan Guard 40mm Metal</td>
<td>Sunon Fans</td>
<td>FG-4</td>
<td>1</td>
<td>$1.42</td>
</tr>
<tr class="even">
<td>25</td>
<td>Cube Standoff</td>
<td>Aluminum M3 Modding Cubes</td>
<td>V1 Tech</td>
<td>N/A</td>
<td>10</td>
<td>$15.00</td>
</tr>
<tr class="odd">
<td>26</td>
<td>M3, 8mm Pan</td>
<td>Passivated 18-8 Stainless Steel<br />
Pan Head Phillips Screws</td>
<td>McMaster-Carr</td>
<td>92000A118</td>
<td>3</td>
<td>$5.51</td>
</tr>
<tr class="even">
<td>27</td>
<td>M3, 8mm Flat</td>
<td>Passivated 18-8 Stainless Steel<br />
Phillips Flat Head Screw</td>
<td>McMaster-Carr</td>
<td>92010A118</td>
<td>19</td>
<td>$5.52</td>
</tr>
<tr class="odd">
<td>28</td>
<td>M3, 5mm Pan</td>
<td>Passivated 18-8 Stainless Steel<br />
Pan Head Phillips Screws</td>
<td>McMaster-Carr</td>
<td>92000A114</td>
<td>8</td>
<td>$5.45</td>
</tr>
<tr class="even">
<td>29</td>
<td>M3, 8mm Standoff F/F</td>
<td>Female Threaded Hex Standoff</td>
<td>McMaster-Carr</td>
<td>94868A164</td>
<td>8</td>
<td>$10.08</td>
</tr>
<tr class="odd">
<td>30</td>
<td>M3, 35mm Standoff M/F</td>
<td>Male-Female Threaded Hex<br />
Standoff</td>
<td>McMaster-Carr</td>
<td>93655A224</td>
<td>8</td>
<td>$39.44</td>
</tr>
<tr class="even">
<td>31</td>
<td>M3, 6mm Standoff M/F</td>
<td>Male-Female Threaded Hex<br />
Standoff</td>
<td>McMaster-Carr</td>
<td>93655A093</td>
<td>4</td>
<td>$15.64</td>
</tr>
<tr class="odd">
<td>32</td>
<td>M3 Nut</td>
<td>18-8 Stainless Steel Hex Nut</td>
<td>McMaster-Carr</td>
<td>91828A211</td>
<td>4</td>
<td>$4.73</td>
</tr>
<tr class="even">
<td>33</td>
<td>M3, 10mm Flat</td>
<td>Passivated 18-8 Stainless Steel<br />
Phillips Flat Head Screw</td>
<td>McMaster-Carr</td>
<td>92010A120</td>
<td>12</td>
<td>$5.91</td>
</tr>
<tr class="odd">
<td>34</td>
<td>M3, 12mm Flat</td>
<td>Passivated 18-8 Stainless Steel<br />
Phillips Flat Head Screw</td>
<td>McMaster-Carr</td>
<td>92010A122</td>
<td>4</td>
<td>$6.04</td>
</tr>
<tr class="even">
<td>35</td>
<td>M3, 30mm Flat</td>
<td>Passivated 18-8 Stainless Steel<br />
Phillips Flat Head Screw</td>
<td>McMaster-Carr</td>
<td>92010A138</td>
<td>4</td>
<td>$10.26</td>
</tr>
<tr class="odd">
<td>36</td>
<td>M4, 18mm Pan</td>
<td>Passivated 18-8 Stainless Steel<br />
Pan Head Phillips Screws</td>
<td>McMaster-Carr</td>
<td>92000A227</td>
<td>4</td>
<td>$12.95</td>
</tr>
<tr class="even">
<td>45</td>
<td>M4 Nut</td>
<td>18-8 Stainless Steel Hex Nut</td>
<td>McMaster-Carr</td>
<td>91828A231</td>
<td>4</td>
<td>$6.59</td>
</tr>
<tr class="odd">
<td>46</td>
<td>4-40, 1/2" Flat</td>
<td>Passivated 18-8 Stainless Steel<br />
Phillips Flat Head Screw</td>
<td>McMaster-Carr</td>
<td>91771A110</td>
<td>2</td>
<td>$6.63</td>
</tr>
<tr class="even">
<td>47</td>
<td>M12 Connector</td>
<td>Micro M12 Screw-Together<br />
Connector</td>
<td>McMaster-Carr</td>
<td>4458N11</td>
<td>3</td>
<td>$58.95</td>
</tr>
<tr class="odd">
<td>48</td>
<td>Locknut</td>
<td>1/2 NPT Black Locknut for Continuous-Flex Plastic Conduit
Fitting</td>
<td>McMaster-Carr</td>
<td>3185K112</td>
<td>3</td>
<td>$2.61</td>
</tr>
<tr class="even">
<td>49</td>
<td>USB A to C</td>
<td>USB AM TO USB C, USB 2.0 - 150MM</td>
<td>Cvilux USA</td>
<td>DH-20M50054</td>
<td>3</td>
<td>$3.87</td>
</tr>
<tr class="odd">
<td>50</td>
<td>Ethernet Cable 1ft</td>
<td>Cable Mod 8P8C Plug to Plug 1ft</td>
<td>Amphenol Cables on Demand</td>
<td>MP-64RJ45UNNY-001</td>
<td>1</td>
<td>$3.81</td>
</tr>
<tr class="even">
<td>51</td>
<td>Ethernet Cable 2ft</td>
<td>Ethernet Cables / Networking Cables CAT 6 UNSHIELDED, BLUE, 2ft</td>
<td>Amphenol Cables on Demand</td>
<td>MP-64RJ45UNNB-002</td>
<td>3</td>
<td>$13.35</td>
</tr>
<tr class="odd">
<td>52</td>
<td>Power Fuse</td>
<td>Fuse Drawer For PWR MOD X-SAFE 2PL</td>
<td>Schurter Inc.</td>
<td>4301.1403</td>
<td>1</td>
<td>$5.61</td>
</tr>
<tr class="even">
<td>53</td>
<td>3 Pin Plug</td>
<td>Term Block Plug 3POS STR 5.08mm</td>
<td>Weidmuller</td>
<td>1943820000</td>
<td>2</td>
<td>$7.36</td>
</tr>
<tr class="odd">
<td>54</td>
<td>14 Pin Plug</td>
<td>Conn RCPT HSG 14POS 3.96mm</td>
<td>Molex</td>
<td>9508143</td>
<td>2</td>
<td>$24.36</td>
</tr>
<tr class="even">
<td>55</td>
<td>2 Pin Plug</td>
<td>CONN RCPT HSG 3POS 3.96MM</td>
<td>Molex</td>
<td>9508033</td>
<td>1</td>
<td>$0.26</td>
</tr>
<tr class="odd">
<td>56</td>
<td>Pins</td>
<td>CONN 18-20AWG CRIMP TIN</td>
<td>Molex</td>
<td>0008520113</td>
<td>31</td>
<td>$8.00</td>
</tr>
<tr class="even">
<td>57</td>
<td>20 Gauge Wire</td>
<td>N/A</td>
<td>N/A</td>
<td>N/A</td>
<td>5ft</td>
<td>$0.00</td>
</tr>
<tr class="odd">
<td>58</td>
<td>Velcro or Zip Ties</td>
<td>Optional</td>
<td>N/A</td>
<td>N/A</td>
<td>N/A</td>
<td>$0.00</td>
</tr>
<tr class="even">
<td colspan="6">Total Cost Per Control Center</td>
<td>$1,737.90</td>
</tr>
</tbody>
</table>

### Side and Top Panel Assemblies

To allow for assembly of the internal components of the PCM, there needs
to be access from the user to get inside the enclosure. The user can do
this by removing the side and top panels of the PCM. Each panel will
have its own subassembly to allow for easy removal and installation of
each panel. The side panel requires the 3D printed rail, three M3, 8mm
pan screws, three cube standoffs, and three M3, 8mm flat screws. The
instructions for the side panel assembly are shown in Figure 11.

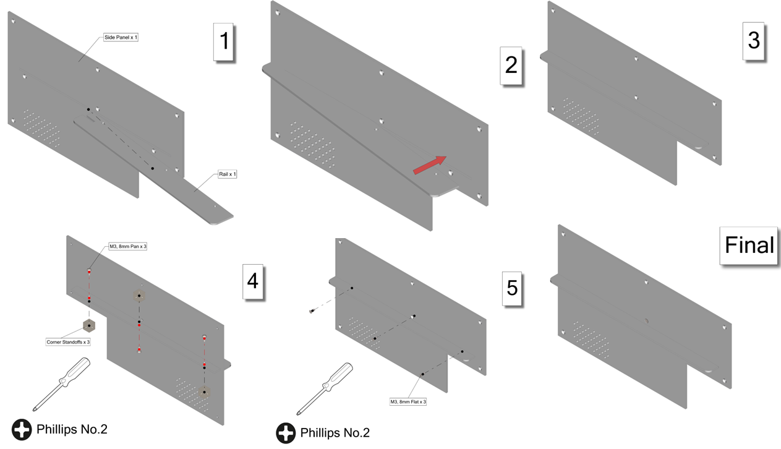
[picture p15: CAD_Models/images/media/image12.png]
{width="6.245833333333334in"
height="3.5900918635170602in"}

Figure 11 The side panel subassembly.

The top panel requires five M3, 8mm flat screws and five cube standoffs.
The top panel assembly is shown in Figure 12.

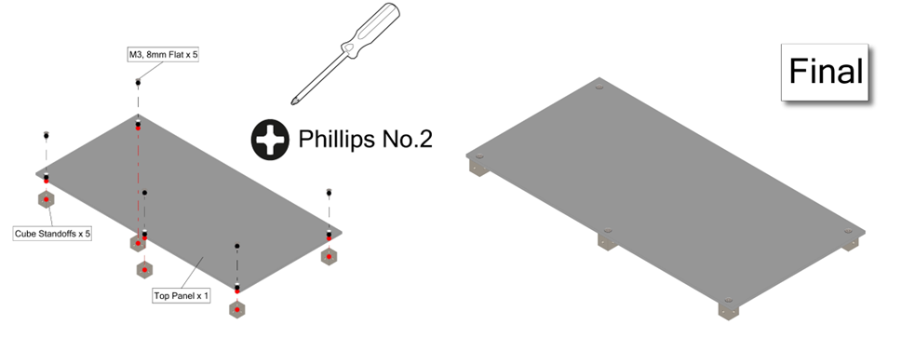
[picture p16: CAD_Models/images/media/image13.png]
{width="5.583333333333333in"
height="2.0915748031496064in"}

Figure 12 The top panel subassembly.

### Electronic Subassemblies

The electronic subassemblies should be assembled before inserting into
the enclosure. The subassemblies will be for the power supply, power
distribution board, and the SBC units. The power supply and power
distribution board assembly each require four M3, 8mm pan screws and
four M3, 8mm standoffs female/female. The power supply and the power
distribution board instructions are shown in Figures 13 and 14.

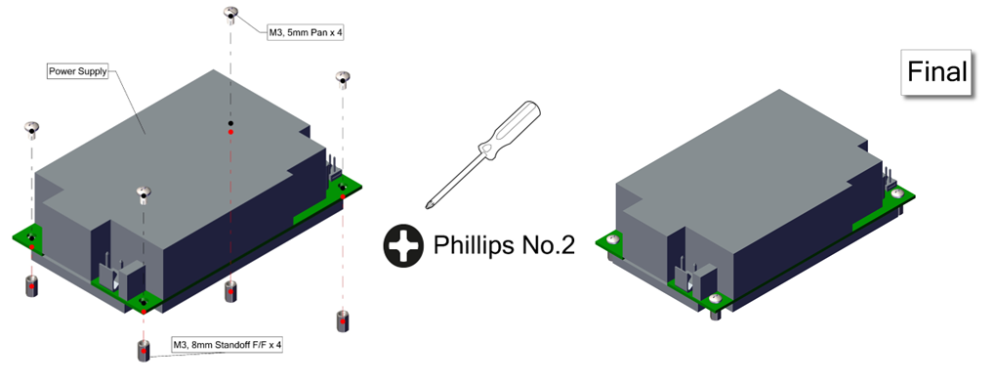
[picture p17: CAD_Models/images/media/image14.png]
{width="6.79375in"
height="2.613888888888889in"}

Figure 13 The power supply subassembly.

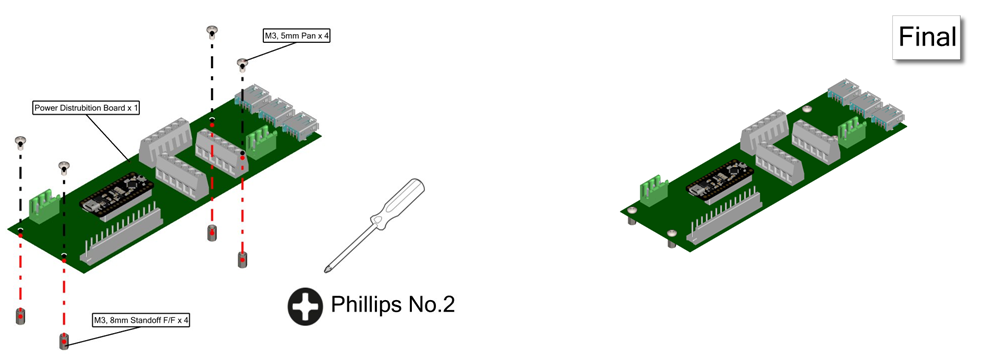
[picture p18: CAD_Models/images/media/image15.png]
{width="6.0in"
height="2.138464566929134in"}

Figure 14 The power distribution board subassembly.

To consolidate space, the three SBC compression units are stacked on one
another using standoffs. To do this, an SBC subassembly must be made.
The subassembly requires eight M3, 35mm standoffs male/female, four M3,
6mm standoffs male/female, and four M3 nuts. All parts can be hand
tightened. The instructions for the SBC subassembly are shown in Figure
15.

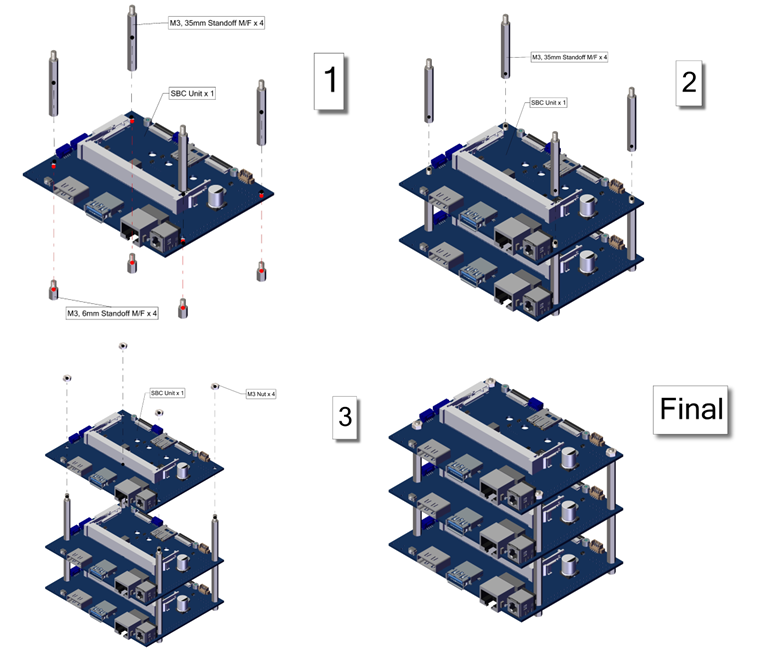
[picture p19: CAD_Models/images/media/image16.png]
{width="5.073611111111111in"
height="4.353472222222222in"}

Figure 15 Compression unit subassembly.

### Main Body Assembly

The next steps involve inserting the subassemblies and other components
into the main body. The first six steps of this process are shown in
figure 16. A No. 2 Phillips screwdriver will be required for these
steps. These steps involve installing all the electronic subassemblies
(SBC, power distribution board, and power supply) plus the switch and
USB mount.

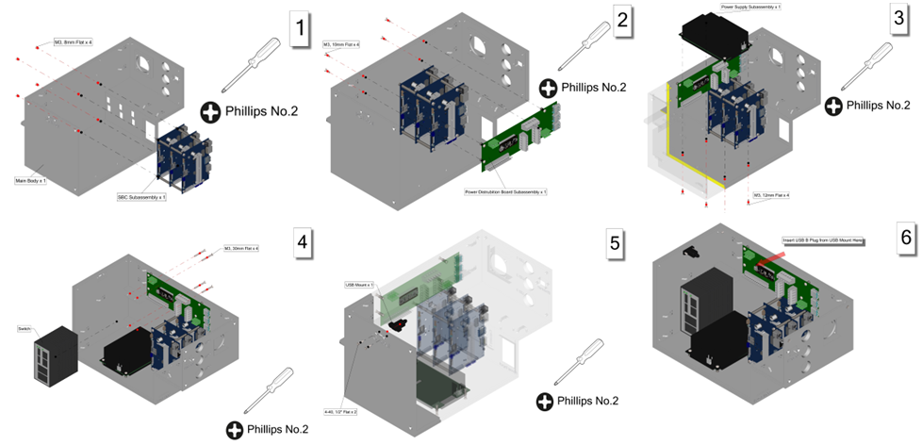
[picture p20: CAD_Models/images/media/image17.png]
{width="6.083333333333333in"
height="2.936066272965879in"}

Figure 16 Steps 1 to 6 of the enclosure assembly.

The next steps will include assembling the fan and wiring for it. A 3
pin plug can be attached to the fan wire to plug into the power
distribution board. There are loops available to organize wires inside
the enclosure. The power mount and ethernet mount will also be assembled
during these steps. The power mount will require a 2 pin plug to be
attached and connected to the power supply. For the 2 pin plug, a hand
crimper (0640160205, Molex, Lisle, IL), pins, and 20 gauge wire will be
needed. Three M12 connectors will also be added and held in place with
locknuts. These steps are shown in Figure 17.

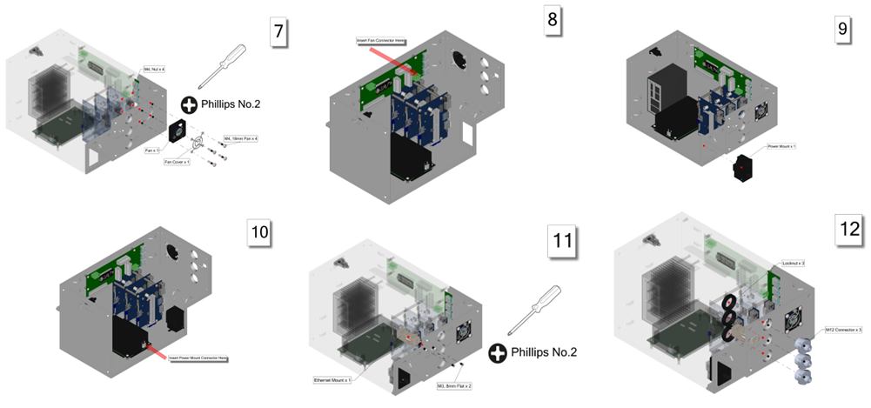
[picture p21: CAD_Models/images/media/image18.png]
{width="6.673611111111111in"
height="3.127083333333333in"}

Figure 17 Steps 7 to 12 of the enclosure assembly.

Step 13 involves wiring the 6 pin connectors to the assigned terminal on
the power distribution board. Steps 14 and 15 are for mounting two
standoff cubes. Step 16 will require a custom cable made from two 14 pin
plugs. The cable will need to have 28 pins, two 14 pin plugs, 20 gauge
wire, and require the Molex hand crimper. Step 17 connects the three SBC
units to the power distribution board using USB A to C cables. Step 18
connects the three SBC units to the switch via 2ft ethernet cables.
Steps 13 to 18 are shown in Figure 18.

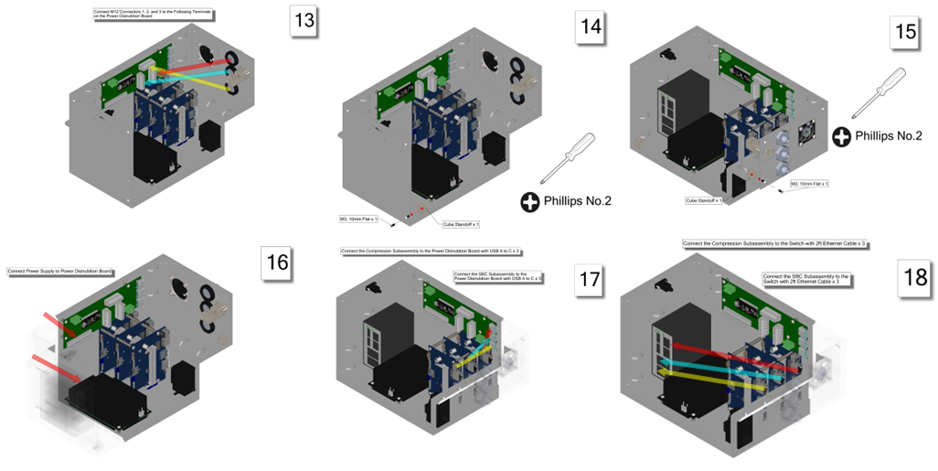
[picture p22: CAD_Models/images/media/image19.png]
{width="6.840277777777778in"
height="3.433333333333333in"}

Figure 18 Steps 13 to 18 of the enclosure assembly.

Step 19 will connect the ethernet mount to the switch via a 1ft cable. A
custom cable with two 3 pin plugs connects the power distribution board
to the switch. The cable will have 6 pins, two 3 pin plugs, 20 gauge
wire and require the Molex crimper. Now all connections inside the PCM
are complete and it is operational. The last two steps will be to
install the side panel and top panel subassemblies to finish the
enclosure. These steps are shown in figure 19. The finished assembly of
the PCM is shown in Figure 20.

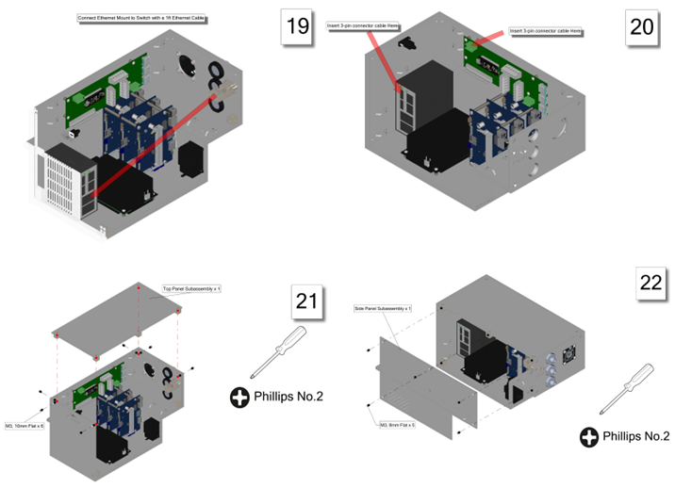
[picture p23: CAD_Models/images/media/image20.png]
{width="4.773611111111111in"
height="3.453472222222222in"}

Figure 19 Steps 19 to 22 of the enclosure assembly.

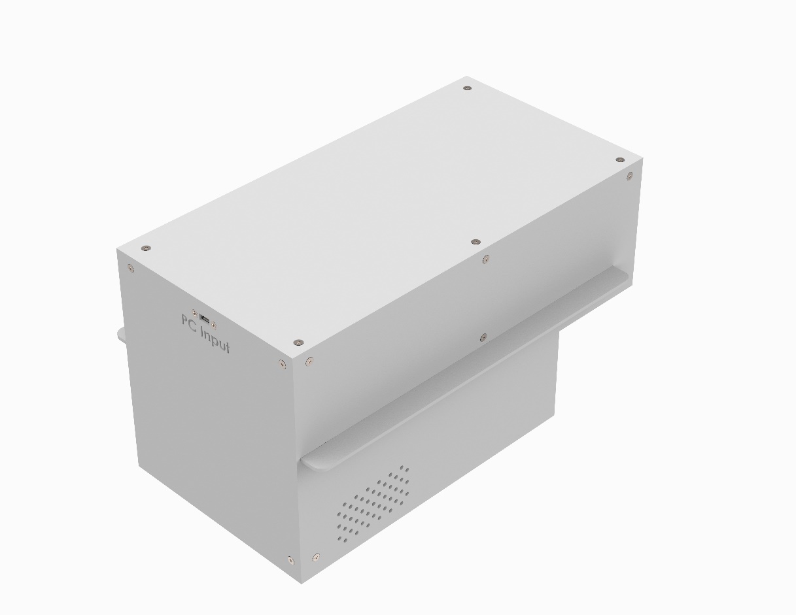
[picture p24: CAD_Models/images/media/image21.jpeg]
{width="5.524133858267716in"
height="3.6969695975503063in"}

Figure 20 Finished PCM assembly.

# Modular Rack Assembly

## Modular Rack Overview

The modular rack is responsible for securing the three Monitoring Cage
units and PCM in place for testing. The rack is non ventilated and is
designed to be used in a high density format. The modular rack setup
will allow for easy removal of Monitoring Cage units for repairs,
maintenance, animal care, etc.

## Modular Rack Fabrication

To assemble the modular rack, several parts will need to be custom
fabricated. Three Runner Support Bars (8975K582, McMaster-Carr,
Elmhurst, IL) will need to be machined. Two Camera Mounting Enclosure Bars (8975K582,
McMaster-Carr, Elmhurst, IL) will also need to be machined. In this
fabrication process, a waterjet was used to fabricate the bars. Two
runner bar brackets will need to be 3D printed. In this fabrication
process, the Markforged X7 (Waltham, MA) was used to print the parts out
of Onyx.

## Modular Rack Assembly

The bill of materials for the assembly of the Modular Rack is shown in
Table 3. Items that were custom made have .STL files to reference on the
Github page. The other items were purchased from vendors.

<table>
<caption><p>Bill of materials for the Modular Rack
assembly.</p></caption>
<colgroup>
<col style="width: 7%" />
<col style="width: 15%" />
<col style="width: 22%" />
<col style="width: 14%" />
<col style="width: 17%" />
<col style="width: 8%" />
<col style="width: 14%" />
</colgroup>
<thead>
<tr class="header">
<th>ITEM NO.</th>
<th>Part Label</th>
<th>Description</th>
<th>Source</th>
<th>Vendor Part Number</th>
<th>Qty</th>
<th>Cost</th>
</tr>
</thead>
<tbody>
<tr class="odd">
<td>1</td>
<td>Cage Runner</td>
<td>NIEHS CAN K10000 Kit, Runners, NexGen, Left/Right, Hardware, Glass
Filled Polysulfone High Temperature Plastic, Purple</td>
<td>Allentown Inc.</td>
<td>K10000</td>
<td>4</td>
<td>$216.00</td>
</tr>
<tr class="even">
<td>2</td>
<td>Cross Bar</td>
<td>1 x 1 x 16.5 inches T-Slotted profile - Four Open T-slots</td>
<td>80/20</td>
<td>8020-1010-black x 16.5</td>
<td>10</td>
<td>$167.90</td>
</tr>
<tr class="odd">
<td>3</td>
<td>Side Bar</td>
<td>1 x 1 x 15.5 inches T-Slotted profile - Four Open T-slots</td>
<td>80/20</td>
<td>8020-1010-black x 15.5</td>
<td>6</td>
<td>$97.62</td>
</tr>
<tr class="even">
<td>4</td>
<td>Vertical Bar</td>
<td>1 x 1 x 30 inches T-Slotted profile - Four Open T-slots</td>
<td>80/20</td>
<td>8020-1010-black x 30</td>
<td>4</td>
<td>$55.24</td>
</tr>
<tr class="odd">
<td>5</td>
<td>Corner Bracket</td>
<td>10 Series 2 Hole - Gusseted Inside Corner Bracket</td>
<td>80/20</td>
<td>8020-4132-black</td>
<td>16</td>
<td>$130.88</td>
</tr>
<tr class="even">
<td>6</td>
<td>1/4"-20, 1/2" Pan</td>
<td>1/4-20 x .500" Button Head Socket Cap Screw (BHSCS)</td>
<td>80/20</td>
<td>8020-3061</td>
<td>38</td>
<td>$12.92</td>
</tr>
<tr class="odd">
<td>7</td>
<td>1/4"-20 T-Nut</td>
<td>1/4-20 Roll-In T-Nut with Ball Spring</td>
<td>80/20</td>
<td>8020-3923</td>
<td>42</td>
<td>$102.48</td>
</tr>
<tr class="even">
<td>8</td>
<td>Camera Mounting Enclosure Bar</td>
<td>24" x 2" x 1/8" (L x W x H) metal bar</td>
<td>McMaster-Carr</td>
<td>8975K582</td>
<td>2</td>
<td>$14.10</td>
</tr>
<tr class="odd">
<td>9</td>
<td>Locking Clamp</td>
<td>10 Series 90 Degree Structural Right Angle Pivot Nub</td>
<td>80/20</td>
<td>8020-4002-black</td>
<td>4</td>
<td>$44.00</td>
</tr>
<tr class="even">
<td>10</td>
<td>Corner Connector</td>
<td>10 series 3-Way Square Corner Connector</td>
<td>80/20</td>
<td>8020-4042-Black</td>
<td>8</td>
<td>$265.84</td>
</tr>
<tr class="odd">
<td>11</td>
<td>1/4"-20, 1" Pan</td>
<td>1/4-20 x 1.000" Low Head Socket Cap Screw (LHSCS)</td>
<td>80/20</td>
<td>8020-3017</td>
<td>24</td>
<td>$18.72</td>
</tr>
<tr class="even">
<td>12</td>
<td>M4 T-Nut</td>
<td>M4 roll-in T-nut with ball spring</td>
<td>80/20</td>
<td>8020-3919</td>
<td>16</td>
<td>$39.04</td>
</tr>
<tr class="odd">
<td>13</td>
<td>M4, 10mm Pan</td>
<td>Black-Oxide Alloy Steel Socket Head Screw M4 x 0.7 mm Thread, 10 mm
Long</td>
<td>McMaster-Carr</td>
<td>91290A144</td>
<td>16</td>
<td>$1.80</td>
</tr>
<tr class="even">
<td>14</td>
<td>Runner Support Bar</td>
<td>36" x 2" x 1/8" (L x W x H) metal bar</td>
<td>McMaster-Carr</td>
<td>8975K582</td>
<td>3</td>
<td>$29.40</td>
</tr>
<tr class="odd">
<td>15</td>
<td>1/4"-20 Washer</td>
<td>Zinc Yellow-Chromate Plated Steel Oversized Washer
Grade 8, for 1/4" Screw Size, 0.281" ID, 0.625" OD</td>
<td>McMaster-Carr</td>
<td>98025A029</td>
<td>1</td>
<td>$0.20</td>
</tr>
<tr class="even">
<td>16</td>
<td>Runner Bar Bracket</td>
<td>3D Printed FDM</td>
<td>3D printed</td>
<td>N/A - refer to STL file</td>
<td>2</td>
<td>$8.00</td>
</tr>
<tr class="odd">
<td>17</td>
<td>1/4"-20, 3/4" Flat</td>
<td>82 Degree Countersink, 1/4"-20 Thread, 3/4" Long, Undercut</td>
<td>McMaster-Carr</td>
<td>96640A286</td>
<td>1</td>
<td>$14.37</td>
</tr>
<tr class="even">
<td colspan="6">Total Cost Per Modular Rack</td>
<td>$1,218.51</td>
</tr>
</tbody>
</table>

#### Rack Top Subassembly

To make the assembly of the modular rack more user friendly, it is best
to assemble subassemblies of the rack. There are three subassemblies:
the rack top, base, mid bar, and rear bar. They can be completed in any
order. For the modular rack, one top subassembly is required. A 1/8",
5/32", and 3/16" Allen key are required for assembly. First the runner
bar bracket will be secured to a cross bar 195mm from the edge of the
crossbar. Second, two corner brackets will be secured to the opposite
side of the cross bar. Next two side bars will slide onto each face end
of the cross bar. Secure the cross bar 312mm offset from one end of the
side bar. Please refer to Figure 21 for steps 1 to 4 of the rack top
subassembly.

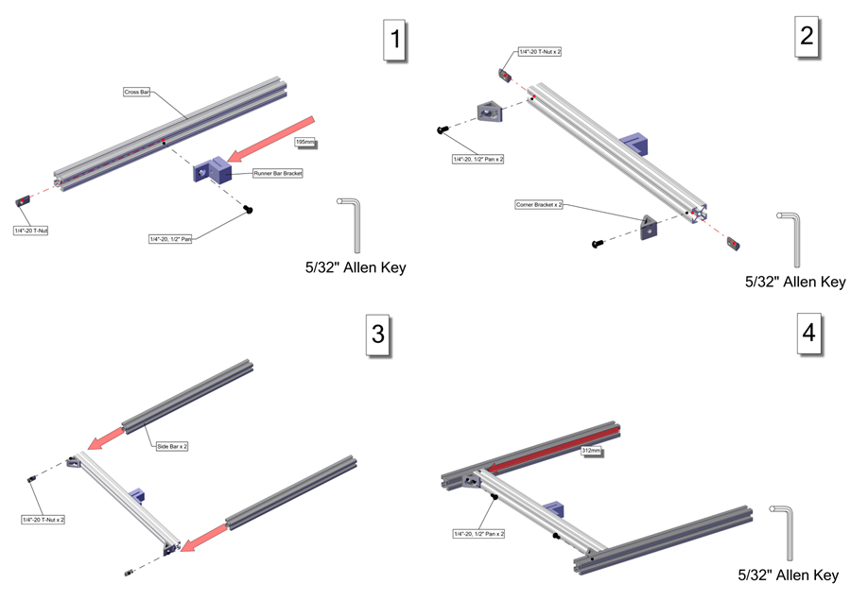
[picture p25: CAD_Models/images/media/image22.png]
{width="5.660661636045495in"
height="4.0in"}

Figure 21 Steps 1 to 4 of the rack top subassembly.

Two ¼"-20 T-Nuts will slide into the inner rails of the side bars. Do
not secure these T-nuts, they will be secured in a later step. Next
slide two T-nuts (a part of the Locking Clamp assembly, P/N
8020-4002-black, Allentown Inc., Allentown, NJ) and an Camera Mounting Enclosure bar on the
inside rails of the side bars. Secure the Camera Mounting Enclosure bar in place
approximately 78mm offset from the side bar face end. The Camera Mounting Enclosure bar is
secured by the rest of the Locking Clamp (P/N 8020-4002-black, Allentown
Inc., Allentown, NJ). Next fasten two corner brackets onto each face end
of two new cross bars. Please refer to Figure 22 for steps 5 to 8 of the
rack top subassembly.

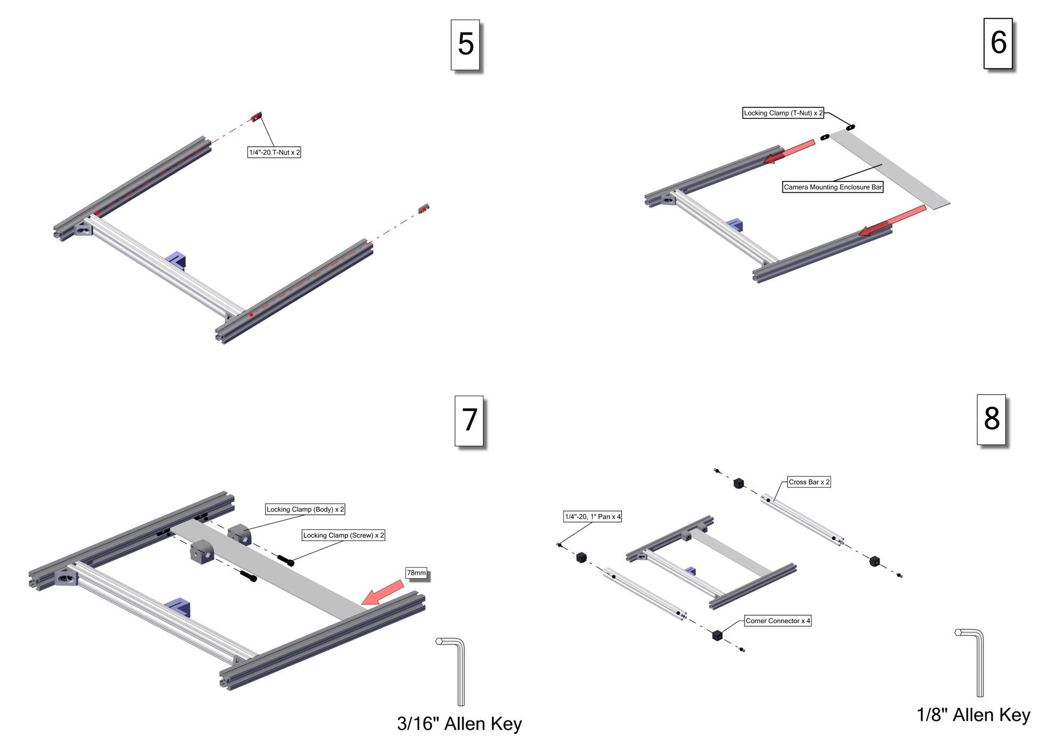
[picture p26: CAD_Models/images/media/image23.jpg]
{width="5.660661636045495in"
height="4.0in"}

Figure 22 Steps 5 to 8 of the rack top subassembly.

The final step involves fastening the cross bars with the corner
connectors to the face ends of the side bars. The final step and
resulting rack top subassembly can be found in Figure 23.

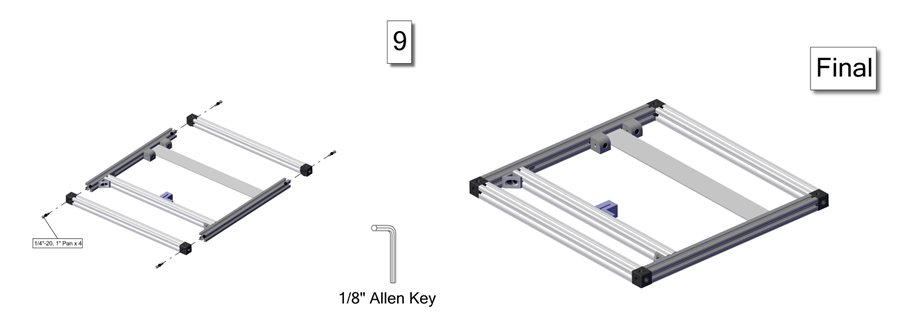
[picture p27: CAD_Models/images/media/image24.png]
{width="6.000694444444444in"
height="2.120138888888889in"}

Figure 23 Step 9 and finished version of the rack top subassembly.

#### Rack Base Subassembly

For the modular rack, one base subassembly is required. A 1/8" and 5/32"
Allen key are required for assembly. First the runner bar bracket will
be secured to a cross bar 195mm from the edge of the crossbar. Second,
two corner brackets will be secured to the opposite side of the cross
bar. Next two side bars will slide onto each face end of the cross bar.
Secure the cross bar 312mm offset from one end of the side bar. Please
refer to Figure 24 for steps 1 to 4 of the rack base subassembly.

{width="5.660661636045495in"
height="4.0in"}

Figure 24 Figure 20 Steps 1 to 4 of the rack base subassembly.

Two ¼"-20 T-Nuts will slide into the inner rails of the side bars. Do
not secure these T-nuts, they will be secured in a later step. Next
fasten two corner brackets onto each face end of two new cross bars. The
final step involves fastening the cross bars with the corner connectors
to the face ends of the side bars. The final steps 5 to 9 and resulting
rack base subassembly can be found in Figure 25.

{width="5.660661636045495in"
height="4.0in"}

Figure 25 Steps 5 to 7 and the finished version of the rack base
subassembly.

#### Rack Mid Bar Subassembly

For the modular rack, one mid bar subassembly is required. A 5/32" and
3/16" Allen key are required for assembly. First slide two T-nuts (a
part of the Locking Clamp assembly, P/N 8020-4002-black, Allentown Inc.,
Allentown, NJ) and an Camera Mounting Enclosure bar on the inside rails of the side bars.
Secure the Camera Mounting Enclosure bar in place approximately 78mm offset from the side
bar face end. The Camera Mounting Enclosure bar is secured by the rest of the Locking Clamp
(P/N 8020-4002-black, Allentown Inc., Allentown, NJ). Next on the bottom
side of the side bars, secure four corner brackets flesh to the face
ends of the side bars. The assembly steps 1 to 3 and resulting rack mid
bar subassembly can be found in Figure 26.

{width="5.660661636045495in"
height="4.0in"}

Figure 26 Assembly steps and the finished version of the rack mid bar
subassembly.

#### Rack Rear Bar Subassembly

Four mid bar subassemblies are required for one modular rack. A 5/32"
Allen key is required for assembly. On the top side of the cross bar,
secure two corner brackets flesh to the face ends of the cross bars.
Next slide four M4 T-Nuts onto the front rail of the cross bar. Do not
secure these t-nuts yet. The assembly steps and resulting rack rear bar
subassembly can be found in Figure 27. Repeat these steps to make four
mid bar subassemblies in total.

{width="6.0in"
height="1.4133169291338583in"}

Figure 27 Assembly steps and the finished version of the rack rear bar
subassembly.

#### Rack Assembly 

Once all the subassemblies are completed for the modular rack, then the
final rack can be assembled. A 1/8", 5/32", and 3mm Allen key and a No.
2 Phillips screwdriver are required for assembly. First fasten the four
vertical bars to the base subassembly. Second, install the mid bar
subassembly and fasten it 350mm above the base subassembly. Next install
one rear bar subassembly between the two rear vertical posts. Make sure
the corner brackets are on the bottom side of the rear bar subassembly
and they are touching the base subassembly. Please refer to Figure 28
for steps 1 to 4 of the rack assembly.

{width="5.660661636045495in"
height="4.0in"}

Figure 28 Steps 1 to 4 of the rack assembly.

The next step is to install the second rear bar sub assembly between the
two rear vertical posts. Make sure the corner brackets are on the top
side of the rear bar subassembly. Leave a 78mm gap between the first and
second rear cross bars. Please refer to Figure 29 for steps 5 to 8 of
the rack assembly.

{width="5.660661636045495in"
height="4.0in"}

Figure 29 Steps 5 to 8 of the rack assembly.

A third rear bar sub assembly will need to be installed between the two
rear vertical posts. Make sure the corner brackets are on the bottom
side of the rear bar subassembly. Leave a 260mm gap between the second
and third rear cross bars. The final rear bar sub assembly will need to
be installed between the two rear vertical posts. Make sure the corner
brackets are on the top side of the rear bar subassembly. Leave a 78 mm
gap between the third and final rear cross bars. Next fasten the top sub
assembly to the top faces of the four vertical bars. Please refer to
Figure 30 for steps 9 to 12 of the rack assembly.

{width="5.660661636045495in"
height="4.0in"}

Figure 30 Steps 9 to 12 of the rack assembly.

Next fasten one runner support to the left side bar on both the top and
base subassemblies. Make sure the runner support bar is square with the
two cross bars on both the top and base subassemblies. Slide another
runner support bar in between the two runner bar brackets and secure
with ¼"-20, ¾" flat screws. Fasten the last runner support to the right
side bar on both the top and base subassemblies. Make sure the runner
support bar is square with the two cross bars on both the top and base
subassemblies. Next install a left and right cage runner. Make sure the
dimples on the runners match with the cutouts on the runner support
bars. The cage runners will be fastened to the M4 T-Nuts in the two
lower rear bar subassemblies. Please refer to Figure 31 for steps 13 to
16 of the rack assembly.

{width="5.660661636045495in"
height="4.0in"}

Figure 31 Steps 13 to 16 of the rack assembly.

Three more sets of a left and right cage runners will need to be
installed. Make sure the dimples on the runners match with the cutouts
on the runner support bars. The cage runners will be fastened to the M4
T-Nuts in the rear bar subassemblies. Please refer to Figure 32 for
steps 17 to 19 and the finished version of the rack assembly.

{width="5.660661636045495in"
height="4.0in"}

Figure 32 Assembly steps 17 to 19 and the finished version of the
modular rack assembly.

# Appendix -- Step by Step Instructions

## Monitoring Cage Assembly

### Hopper Assembly

Diagram, engineering drawing Description automatically generated{width="5.657298775153106in"
height="4.0in"}

Diagram, engineering drawing Description automatically generated{width="5.6572976815398075in"
height="4.0in"}

Diagram, engineering drawing Description automatically generated{width="5.657298775153106in"
height="4.0in"}

Diagram, engineering drawing Description automatically generated{width="5.6572976815398075in"
height="4.0in"}

### Camera Mounting Enclosure Assembly 

Chart, radar chart Description automatically generated{width="5.657298775153106in"
height="4.0in"}

Diagram, engineering drawing Description automatically generated{width="5.657298775153106in"
height="4.0in"}

Diagram, engineering drawing Description automatically generated{width="5.657298775153106in"
height="4.0in"}

Diagram, engineering drawing Description automatically generated{width="5.657298775153106in"
height="4.0in"}

Diagram, engineering drawing Description automatically generated{width="5.657298775153106in"
height="4.0in"}

Diagram, engineering drawing Description automatically generated{width="5.657298775153106in"
height="4.0in"}

Diagram Description automatically generated{width="5.657298775153106in"
height="4.0in"}

Diagram, engineering drawing Description automatically generated{width="5.657298775153106in"
height="4.0in"}

Engineering drawing Description automatically generated{width="5.657298775153106in"
height="4.0in"}

### Monitoring Cage Unit Assembly

Diagram, engineering drawing Description automatically generated{width="5.657298775153106in"
height="4.0in"}Diagram, engineering drawing Description automatically generated{width="5.657298775153106in"
height="4.0in"}Diagram, engineering drawing Description automatically generated{width="5.657298775153106in"
height="4.0in"}A picture containing text, scale, device Description automatically generated{width="5.657298775153106in"
height="4.0in"}Engineering drawing Description automatically generated{width="5.657298775153106in"
height="4.0in"}

## Power and Control Module (PCM) 

[]{#_Toc147213275 .anchor}Side Panel Subassembly

A picture containing text, hinge, metalware Description automatically generated{width="5.356178915135608in"
height="4.0in"}Engineering drawing Description automatically generated{width="6.742818241469816in"
height="4.0in"}

Arrow Description automatically generated{width="6.427409230096238in"
height="4.0in"}Diagram Description automatically generated{width="5.678094925634296in"
height="4.0in"}{width="5.531424978127734in"
height="4.0in"}Arrow Description automatically generated{width="6.640029527559055in"
height="4.0in"}

### Top Panel Subassembly

Chart, schematic Description automatically generated{width="5.131104549431321in"
height="4.0in"}A picture containing accessory, table, worktable Description automatically generated{width="6.291666666666667in"
height="3.9993055555555554in"}

### Power Supply Subassembly

Diagram Description automatically generated{width="6.7728291776028in"
height="4.0in"}

{width="5.6571205161854765in"
height="4.0in"}

### Power Distribution Board Subassembly

Diagram Description automatically generated{width="6.439989063867016in"
height="4.0in"}

A picture containing text, electronics, circuit Description automatically generated{width="5.6571205161854765in"
height="4.0in"}

### SBC Subassembly

Diagram, engineering drawing Description automatically generated{width="6.04759842519685in"
height="4.0in"}Diagram, engineering drawing Description automatically generated{width="5.6571205161854765in"
height="4.0in"}

Diagram, engineering drawing Description automatically generated{width="5.6571205161854765in"
height="4.0in"}Diagram, engineering drawing Description automatically generated{width="6.366107830271216in"
height="4.0in"}

### PCM Main Body Assembly

Diagram Description automatically generated{width="6.540286526684165in"
height="4.0in"}Diagram, engineering drawing Description automatically generated{width="6.34078302712161in"
height="4.0in"}Diagram Description automatically generated{width="5.9089041994750655in"
height="4.0in"}A diagram of a house Description automatically generated with medium confidence{width="5.7615901137357834in"
height="4.0in"}A diagram of a house Description automatically generated with low confidence{width="5.6571205161854765in"
height="4.0in"}A picture containing text, electronics, businesscard Description automatically generated{width="6.52629593175853in"
height="4.0in"}Diagram, engineering drawing Description automatically generated{width="5.657119422572179in"
height="4.0in"}Diagram, engineering drawing Description automatically generated{width="6.069858923884515in"
height="4.0in"}A picture containing electronics Description automatically generated{width="5.657119422572179in"
height="4.0in"}Diagram, engineering drawing Description automatically generated{width="6.165812554680665in"
height="4.0in"}A diagram of a house Description automatically generated with medium confidence{width="5.657119422572179in"
height="4.0in"}A picture containing electronics, jack Description automatically generated{width="6.595985345581802in"
height="4.0in"}Diagram, engineering drawing Description automatically generated{width="5.954010279965004in"
height="4.0in"}Diagram, engineering drawing Description automatically generated{width="5.657119422572179in"
height="4.0in"}

A diagram of a house Description automatically generated with medium confidence{width="6.459422572178478in"
height="4.0in"}Diagram, engineering drawing Description automatically generated{width="6.379686132983377in"
height="4.0in"}A picture containing toy, electronics Description automatically generated{width="6.554414916885389in"
height="4.0in"}{width="6.252307524059493in"
height="4.0in"}

Diagram, engineering drawing Description automatically generated{width="6.071262029746282in"
height="4.0in"}Diagram, engineering drawing Description automatically generated{width="5.657119422572179in"
height="4.0in"}A diagram of a house Description automatically generated with low confidence{width="5.6571205161854765in"
height="4.0in"}Diagram, engineering drawing Description automatically generated{width="6.347713254593176in"
height="4.0in"}A picture containing text, electronics, jack Description automatically generated{width="5.657119422572179in"
height="4.0in"}

## Modular Rack Assembly

### Rack Top Subassembly

Diagram, engineering drawing Description automatically generated{width="5.657298775153106in"
height="4.0in"}{width="5.657298775153106in"
height="4.0in"}Diagram Description automatically generated with medium confidence{width="5.657298775153106in"
height="4.0in"}Diagram Description automatically generated{width="5.657298775153106in"
height="4.0in"}Diagram Description automatically generated with low confidence{width="5.657298775153106in"
height="4.0in"}Diagram Description automatically generated{width="5.657298775153106in"
height="4.0in"}Diagram, engineering drawing Description automatically generated{width="5.657298775153106in"
height="4.0in"}{width="5.657298775153106in"
height="4.0in"}{width="5.657298775153106in"
height="4.0in"}{width="5.657298775153106in"
height="4.0in"}

### Rack Base Subassembly

Diagram, engineering drawing Description automatically generated{width="5.657298775153106in"
height="4.0in"}Diagram Description automatically generated{width="5.657298775153106in"
height="4.0in"}Diagram Description automatically generated with medium confidence{width="5.657298775153106in"
height="4.0in"}Diagram Description automatically generated{width="5.657298775153106in"
height="4.0in"}Diagram Description automatically generated with low confidence{width="5.657298775153106in"
height="4.0in"}Diagram Description automatically generated{width="5.657298775153106in"
height="4.0in"}Diagram, engineering drawing Description automatically generated{width="5.657298775153106in"
height="4.0in"}Text, engineering drawing, whiteboard Description automatically generated{width="5.657298775153106in"
height="4.0in"}

### Rack Mid Bar Subassembly 

Diagram Description automatically generated{width="5.657298775153106in"
height="4.0in"}Diagram, engineering drawing Description automatically generated{width="5.657298775153106in"
height="4.0in"}Diagram Description automatically generated{width="5.657298775153106in"
height="4.0in"}Text, whiteboard Description automatically generated{width="5.657298775153106in"
height="4.0in"}

### Rack Rear Bar Subassembly

Diagram Description automatically generated{width="5.657458442694663in"
height="4.0in"}

Diagram Description automatically generated with medium confidence{width="5.657458442694663in"
height="4.0in"}

A picture containing text, wrench, tool Description automatically generated{width="5.657298775153106in"
height="4.0in"}

### Rack Assembly 

Chart Description automatically generated with medium confidence{width="5.657298775153106in"
height="4.0in"}Diagram Description automatically generated{width="5.657298775153106in"
height="4.0in"}Diagram Description automatically generated{width="5.657298775153106in"
height="4.0in"}Diagram Description automatically generated{width="5.657298775153106in"
height="4.0in"}Diagram, engineering drawing Description automatically generated{width="5.657298775153106in"
height="4.0in"}Diagram Description automatically generated{width="5.657298775153106in"
height="4.0in"}Diagram, engineering drawing Description automatically generated{width="5.657298775153106in"
height="4.0in"}Diagram Description automatically generated{width="5.657298775153106in"
height="4.0in"}A picture containing text, handcart Description automatically generated{width="5.657298775153106in"
height="4.0in"}Diagram Description automatically generated{width="5.657298775153106in"
height="4.0in"}Diagram, engineering drawing Description automatically generated{width="5.657298775153106in"
height="4.0in"}Diagram, engineering drawing Description automatically generated{width="5.657298775153106in"
height="4.0in"}Diagram Description automatically generated{width="5.657298775153106in"
height="4.0in"}Diagram Description automatically generated{width="5.657298775153106in"
height="4.0in"}Diagram Description automatically generated{width="5.657298775153106in"
height="4.0in"}Diagram Description automatically generated{width="5.657298775153106in"
height="4.0in"}Diagram Description automatically generated{width="5.657298775153106in"
height="4.0in"}Chart Description automatically generated with low confidence{width="5.657298775153106in"
height="4.0in"}Diagram Description automatically generated{width="5.657298775153106in"
height="4.0in"}A picture containing handcart Description automatically generated{width="5.657298775153106in"
height="4.0in"}

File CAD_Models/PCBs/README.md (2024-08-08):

Power distribution printed circuirt board.  Altium files and gerber files.

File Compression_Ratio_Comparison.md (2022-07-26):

All of the following were captured in real-time, 30 fps from the bag file play back.
All of the following are 1280x720 dimensions

## One_Mouse_5_minutes_depth.bag
5 minutes
LSB libx264 YUV420P10LE 
## CRF 7
Average PSNR 82
Compression Ratio 9.5

## CRF 10 
Average PSNR 80 dB
Compression Ratio 10

## CRF 15
Average PSNR 76 dB
Compression Ratio 12

## CRF 17
Average PSNR 74 dB
Compression Ratio 13

## CRF 19

## CRF 21
Average PSNR 70 dB
Compression Ratio 17

## CRF 25
Average PSNR 65 dB
Compression Ratio 21

## fishy-fish.bag file
24 seconds

### CRF 7
LSBs libx264, YUV420P10LE, crf 7
MSBs libx264rgb, in red channel, RGB, lossless

No B-frames
Average PSNR: 84.2052
Compression ratio is: 15.3366

2 B-frames
Average PSNR: 84.8591
Compression ratio is: 15.7475

### CRF 10

LSBs libx264, YUV420P10LE, crf 10
MSBs libx264rgb, in red channel, RGB, lossless

No B-frames
Average PSNR: 82.2046
Compression ratio is: 17.6731

2 B-frames
Average PSNR: 82.6103
Compression ratio is: 18.1305

### CRF 22

LSBs libx264, YUV420P10LE, crf 22
MSBs libx264rgb, in red channel, RGB, lossless

No B-frames
Average PSNR: 72.4221
Compression ratio is: 32.2732

2 B-frames
Average PSNR: 72.3042
Compression ratio is: 33.4647

### CRF 26

LSBs libx264, YUV420P10LE, crf 26
MSBs libx264rgb, in red channel, RGB, lossless

No B-frames
Average PSNR: 68.7074
Compression ratio is: 43.1025

2 B-frames
Average PSNR: 68.5294
Compression ratio is: 45.1862

## plant.bag file
No B-frames
depth_unit 500 (0.5)
LSBs libx264, YUV420P10LE,
MSBs libx264rgb, in red channel, RGB, lossless
11 seconds

### CRF 10
Average PSNR: 81.6879
Compression ratio is: 16.3969

### CRF 22
Average PSNR: 71.5518
Compression ratio is: 29.2623

### CRF 26
Average PSNR: 67.756
Compression ratio is: 40.1176

## floating_mug.bag
No B-frames
8 seconds
depth_unit 1000 (1.0)
LSBs libx264, YUV420P10LE,
MSBs libx264rgb, in red channel, RGB, lossless

### CRF 10
Average PSNR: 84.9641
Compression ratio is: 24.1858

### CRF 14 
Average PSNR: 81.8582
Compression ratio is: 29.325

### CRF 22
Average PSNR: 74.7282
Compression ratio is: 47.4428

### CRF 26
Average PSNR: 70.9032
Compression ratio is: 68.2798

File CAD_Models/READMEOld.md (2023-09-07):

# System for Continuous Observation of Rodents in Home-cage Environment (SCORHE) Instructions for Assembly



# Table of Contents

[SCORHE System Overview
[4](#scorhe-system-overview)](#scorhe-system-overview)

[The SAHM Assembly [4](#the-sahm-assembly)](#the-sahm-assembly)

[SAHM Overview [4](#sahm-overview)](#sahm-overview)

[SAHM Fabrication [5](#sahm-fabrication)](#sahm-fabrication)

[Modified Lid Fabrication
[5](#modified-lid-fabrication)](#modified-lid-fabrication)

[Hopper Fabrication [5](#hopper-fabrication)](#hopper-fabrication)

[Igloo Fabrication [5](#igloo-fabrication)](#igloo-fabrication)

[SAHM Assembly [6](#sahm-assembly)](#sahm-assembly)

[Hopper Assembly [7](#hopper-assembly)](#hopper-assembly)

[Igloo Assembly [8](#igloo-assembly)](#igloo-assembly)

[Finished SAHM Unit Assembly
[10](#finished-sahm-unit-assembly)](#finished-sahm-unit-assembly)

[The Control Center Assembly
[12](#the-control-center-assembly)](#the-control-center-assembly)

[Control Center Overview
[12](#control-center-overview)](#control-center-overview)

[System Fabrication [13](#system-fabrication)](#system-fabrication)

[Enclosure Fabrication
[13](#enclosure-fabrication)](#enclosure-fabrication)

[Control Center Assembly
[13](#control-center-assembly)](#control-center-assembly)

[Side and Top Panel Assemblies
[16](#side-and-top-panel-assemblies)](#side-and-top-panel-assemblies)

[Electronic Subassemblies
[17](#electronic-subassemblies)](#electronic-subassemblies)

[Main Body Assembly [19](#main-body-assembly)](#main-body-assembly)

[Modular Rack Assembly
[23](#modular-rack-assembly)](#modular-rack-assembly)

[Modular Rack Overview
[23](#modular-rack-overview)](#modular-rack-overview)

[Modular Rack Fabrication
[23](#modular-rack-fabrication)](#modular-rack-fabrication)

[Modular Rack Assembly
[23](#modular-rack-assembly-1)](#modular-rack-assembly-1)

[Appendix – Step by Step Instructions
[35](#appendix-step-by-step-instructions)](#appendix-step-by-step-instructions)

[SAHM Assembly [35](#sahm-assembly-1)](#sahm-assembly-1)

[Hopper Assembly [35](#hopper-assembly-1)](#hopper-assembly-1)

[Igloo Assembly [37](#igloo-assembly-1)](#igloo-assembly-1)

[SAHM Unit Assembly [42](#sahm-unit-assembly)](#sahm-unit-assembly)

[Control Center [44](#control-center)](#control-center)

[Side Panel Subassembly [44](#_Toc144982149)](#_Toc144982149)

[Top Panel Subassembly
[48](#top-panel-subassembly)](#top-panel-subassembly)

[Power Supply Subassembly
[49](#power-supply-subassembly)](#power-supply-subassembly)

[Power Distribution Board Subassembly
[50](#power-distribution-board-subassembly)](#power-distribution-board-subassembly)

[SBC Subassembly [51](#sbc-subassembly)](#sbc-subassembly)

[Control Center Main Body Assembly
[53](#control-center-main-body-assembly)](#control-center-main-body-assembly)

[Modular Rack Assembly
[65](#modular-rack-assembly-2)](#modular-rack-assembly-2)

[Rack Top Subassembly
[65](#rack-top-subassembly-1)](#rack-top-subassembly-1)

[Rack Base Subassembly
[70](#rack-base-subassembly-1)](#rack-base-subassembly-1)

[Rack Mid Bar Subassembly
[74](#rack-mid-bar-subassembly-1)](#rack-mid-bar-subassembly-1)

[Rack Rear Bar Subassembly
[76](#rack-rear-bar-subassembly-1)](#rack-rear-bar-subassembly-1)

[Rack Assembly [78](#rack-assembly-1)](#rack-assembly-1)

# 

# SCORHE System Overview

The System for Continuous Observation of Rodents in Home-Cage
Environment (SCORHE) is an open-source system for housing and monitoring
rodents for experiments. The SCORHE system fits inside a custom modular
rack that houses all the components for running the system. The
monitoring cages or Open-Source System for Automated Home-cage
Monitoring (SAHM) units are where the rodents are monitored. There are
three SAHM units per SCORHE system. Each SAHM unit has subassemblies
including an Igloo and Hopper that must be assembled. The Igloo supports
the camera and LEDs above the mouse lid. The hopper is specially
designed to fit into the mouse cages and supply food and water. One
Control Center will need to be fabricated for every SCORHE system. The
Control Center is responsible for powering and housing electronics to
run the SCORHE system. Figure 1 shows the components of the SCORHE
system.

Diagram Description automatically generated

Figure Fully assembled SCORHE system.

This document is organized into subassemblies to build the final SCORHE
system. Each subassembly has a fabrication and assembly section. Each
subassembly has a bill of materials for one subassembly unit. In the
appendix, larger figures of all assembly steps are shown.

# The SAHM Assembly

## SAHM Overview

The Open-Source System for Automated Home-cage Monitoring (SAHM) units
are where the rodents are monitored. These instructions are for one SAHM
unit and must be repeated two more times for each SCORHE system. The
SAHM unit has subassemblies called the Igloo and Hopper that must be
assembled before assembling the final SAHM unit.

Diagram Description automatically generated

Figure The final SAHM unit Assembly

## SAHM Fabrication

### Modified Lid Fabrication

A solid clear NexGen lid (P/N: 228790-1, Allentown Inc, Allentown, NJ)
will need to be modified to support the SAHM system. A DXF file can be
found on the Github page, and it will need to cut into the lid. In this
fabrication process, a waterjet was used to make the cuts into the lid.
In this process, a single pass of the waterjet was used even for the
varying heights of the lid.

### Hopper Fabrication

The two-compartment hopper was designed to house food pellets and a
water bottle inside the NexGen standard cage (P/N: 223581-4, Allentown
Inc, Allentown, NJ). The hopper must be injection molded (ICOMold Inc.,
Hartland, WI) from a food safe, autoclavable material (PSU Ultrason
S3010, BASF, Ludwigshafen, Germany). The food grate (304SS, 26-gauge,
Yarde Metal, White Marsh, MD) is fabricated with a waterjet and bending
tool. The bottle holder (304SS, 24-gauge, Yarde Metal, White Marsh, MD)
is fabricated with a waterjet.

### Igloo Fabrication

The igloo consists of five clear acrylic panels fixed together to
support a camera above the mouse cage. The acrylic panels (Clear Cast
Acrylic-1/4”, Piedmont Plastics, Elkridge, Maryland) must be cut. In
this fabrication process a CO<sub>2</sub> laser cutter (PLS6.150D,
Universal Laser Systems) was used for cutting the panels. Holes on the
panels will need to be countersink with a 90° Countersink drill bit. Two
holes on the top panel will need to be tapped for 4-40 threads. The
handle and camera bracket will need to be 3D printed. In this
fabrication process, the Markforged X7 (Waltham, MA) was used to print
the parts out of Onyx.

## SAHM Assembly

The bill of materials for the assembly of one SAHM unit is shown in
Table 1. The mouse cage lid must be modified before assembling the SAHM
unit. Items that were custom made have .STP or .DXF or .STL files to
reference on the Github page. All other items were purchased from
vendors.

<table>
<caption><p>Bill of materials for the assembly of one SAHM
unit.</p></caption>
<colgroup>
<col style="width: 7%" />
<col style="width: 15%" />
<col style="width: 22%" />
<col style="width: 14%" />
<col style="width: 17%" />
<col style="width: 8%" />
<col style="width: 14%" />
</colgroup>
<tbody>
<tr class="odd">
<td>ITEM NO.</td>
<td>Part Label</td>
<td>Description</td>
<td>Source</td>
<td>Vendor Part Number</td>
<td>Qty</td>
<td>Cost</td>
</tr>
<tr class="even">
<td>1</td>
<td>Mouse Cage Base</td>
<td>MOUSE, XJ/NEXGEN, CLEAR POLYSULFONE HIGH TEMPERATURE PLASTIC, WHITE
AIR KUP</td>
<td>Allentown Inc.</td>
<td>223581-4</td>
<td>1</td>
<td>$48.60</td>
</tr>
<tr class="odd">
<td>2</td>
<td>Mouse Cage Lid</td>
<td>MICRO BARRIER TOP, MOUSE, NEXGEN, SOLID, CLEAR POLYSULFONE HIGH
TEMPERATURE PLASTIC, NO LOCKS</td>
<td>Allentown Inc.</td>
<td>228790-1</td>
<td>1</td>
<td>$139.50</td>
</tr>
<tr class="even">
<td>3</td>
<td>Water bottle</td>
<td> Bottle Udel 9 oz., Ink with "O" Ring</td>
<td>Thoren Caging Systems, Inc.</td>
<td>BW09UIRNO</td>
<td>1</td>
<td>$7.11</td>
</tr>
<tr class="odd">
<td>4</td>
<td>Sipper Tube</td>
<td>Stainless steel with 2 1/2" welded bent sipper tube</td>
<td>Thoren Caging Systems, Inc.</td>
<td>BWCS250HSB</td>
<td>1</td>
<td>$3.79</td>
</tr>
<tr class="even">
<td>5</td>
<td>Hopper</td>
<td>PSU Ultrason S3010</td>
<td>Injection Molded</td>
<td>N/A - refer to STP file</td>
<td>1</td>
<td>$92.19</td>
</tr>
<tr class="odd">
<td>6</td>
<td>Stainless Steel Grommet</td>
<td>Stainless Steel Fabric Grommets with Washer</td>
<td>McMaster-Carr</td>
<td>96015K33</td>
<td>1</td>
<td>$16.68</td>
</tr>
<tr class="even">
<td>7</td>
<td>Food Grate</td>
<td>304SS, 26 Gauge stock piece</td>
<td>Waterjet Cut</td>
<td>N/A - refer to DXF file</td>
<td>1</td>
<td></td>
</tr>
<tr class="odd">
<td>8</td>
<td>Bottle Holder</td>
<td>304SS, 24 Gauge stock piece</td>
<td>Waterjet Cut</td>
<td>N/A - refer to DXF file</td>
<td>1</td>
<td></td>
</tr>
<tr class="even">
<td>9</td>
<td>4-40, 3/8" Flat</td>
<td>Passivated 18-8 Stainless Steel Phillips Flat Head Screw</td>
<td>McMaster-Carr</td>
<td>91099A165</td>
<td>2</td>
<td>$5.55</td>
</tr>
<tr class="odd">
<td>10</td>
<td>Camera</td>
<td>Depth Camera D435</td>
<td>Intel Inc.</td>
<td>D435</td>
<td>1</td>
<td>$314.00</td>
</tr>
<tr class="even">
<td>11</td>
<td>Camera Bracket</td>
<td>3D Printed FDM</td>
<td>3D printed</td>
<td>N/A - refer to STL file</td>
<td>1</td>
<td>$3.00</td>
</tr>
<tr class="odd">
<td>12</td>
<td>1/4"-20, 3/8" Flat</td>
<td>Passivated 18-8 Stainless Steel Phillips Flat Head Screw</td>
<td>McMaster-Carr</td>
<td>91771A535</td>
<td>1</td>
<td>$12.13</td>
</tr>
<tr class="even">
<td>13</td>
<td>1/4"-20 Nut</td>
<td>18-8 Stainless Steel Thin Hex Nut</td>
<td>McMaster-Carr</td>
<td>91847A029</td>
<td>2</td>
<td>$6.36</td>
</tr>
<tr class="odd">
<td>14</td>
<td>1/4"-20, 7/8" Flat</td>
<td>Passivated 18-8 Stainless Steel Phillips Flat Head Screw</td>
<td>McMaster-Carr</td>
<td>91099A478</td>
<td>2</td>
<td>$12.99</td>
</tr>
<tr class="even">
<td>15</td>
<td>Handle</td>
<td>3D Printed FDM</td>
<td>3D printed</td>
<td>N/A - refer to STL file</td>
<td>1</td>
<td>$10.00</td>
</tr>
<tr class="odd">
<td>16</td>
<td>M3, 10mm Flat</td>
<td>316 Stainless Steel Phillips Flat Head Screw</td>
<td>McMaster-Carr</td>
<td>91801A156</td>
<td>12</td>
<td>$9.91</td>
</tr>
<tr class="even">
<td>17</td>
<td>Igloo Front Panel</td>
<td>Cut from 12"x24"x1/4" Clear Cast Acrylic</td>
<td>Laser Cut</td>
<td>N/A - refer to DXF file</td>
<td>1</td>
<td>$13.00</td>
</tr>
<tr class="odd">
<td>18</td>
<td>Igloo Side Panel</td>
<td>Cut from 12"x24"x1/4" Clear Cast Acrylic</td>
<td>Laser Cut</td>
<td>N/A - refer to DXF file</td>
<td>2</td>
<td>$13.00</td>
</tr>
<tr class="even">
<td>19</td>
<td>Igloo Top Panel</td>
<td>Cut from 12"x24"x1/4" Clear Cast Acrylic</td>
<td>Laser Cut</td>
<td>N/A - refer to DXF file</td>
<td>1</td>
<td>$13.00</td>
</tr>
<tr class="odd">
<td>20</td>
<td>Cube Standoff</td>
<td>Aluminum M3 Modding Cubes</td>
<td>V1 Tech</td>
<td>N/A</td>
<td>4</td>
<td>$5.00</td>
</tr>
<tr class="even">
<td colspan="6">Total Cost Per SAHM Unit</td>
<td>$725.81</td>
</tr>
</tbody>
</table>

Bill of materials for the assembly of one SAHM unit.

### Hopper Assembly 

The hopper sub assembly should be completed before inserting into the
SAHM unit. The first step involves using a hammer-driven punch (9612K28,
McMaster-Carr, Elmhurst, IL) to lock the stainless steel grommet in
place. The food grate is then inserted and locked in by two tabs.
Lastly, the bottle holder is inserted and locked in via tabs. The hopper
assembly instructions are shown in Figure 3.



Figure The Hopper sub assembly.

### Igloo Assembly 

The igloo sub assembly must be completed before inserting into the SAHM
unit. A Phillips no. 2 screwdriver will be required for fastening all
screws in this section. The first four steps in the igloo assembly are
shown in Figure 4. Four cube standoffs will be fastened to the top panel
with four M3, 10mm flat screws. The rear panel will be secured via two
M3, 10mm flat screws. Next, the 2 side panels will be secured by two M3,
10mm flat screws for each panel.



Figure Steps 1 to 4 of the Igloo sub assembly.

The next step is to fasten the front panel with two M3, 10mm flat
screws. The handle will be secured in place via two ¼”-20, 7/8” flat
screws and two ¼”-20 nuts. The camera is bolted to the camera bracket by
a ¼”-20, 3/8” flat screw. Two 4-40, 3/8” screws are used to fasten the
camera bracket to the igloo. These steps are shown in Figure 5. The
final igloo sub assembly is shown in Figure 6.



Figure Steps 5 to 8 for the Igloo sub assembly.

Engineering drawing Description automatically generated

Figure The final Igloo sub assembly.

### Finished SAHM Unit Assembly 

Once the hopper and igloo assemblies are completed, the SAHM unit can be
constructed. Four steps are required in this process, and they are shown
in Figure 7. The first step is to insert the hopper near the front of
the mouse cage base. Next, the water bottle is inserted into the hopper.
The third step involves securing the hopper in place via a tab on the
mouse cage lid. The blue arrow in step 3 shows the locking tab. The last
step is to insert the igloo to the mouse cage lid by aligning the four
cutouts shown via 4 red arrows. The final SAHM assembly is shown in
Figure 8.



Figure The steps to complete the SAHM assembly.

Engineering drawing Description automatically generated

Figure The final SAHM assembly.

# The Control Center Assembly

## Control Center Overview

The Control Center is responsible for powering, controlling, and data
communication with three SAHM systems to successfully monitor the
rodents. The Control Center is designed to slide into one of the open
slots on the custom racks using 3D printed rails. The Control Center
will have electronic connections in the rear to the three SAHM systems.
Each Control Center has three single board computers (SBC)
(70878-AI-TX2, Auvidea Denklingen, Germany) utilized as compression
units compressing data from one of the SAHM units and sends the data via
ethernet to the network switch (EH2306, ATOP Technologies, Zhubei City,
Taiwan) inside the Control Center. The switch relays the data to an
ethernet panel mount (MRJ-5780-01, Amphenol ICC, Wallingford, CT) on the
Control Center that can be sent to an external storage system for the
user. The Control Center has a power supply (MPB125-4350G, Bel Power
Solutions, New Jersey City, NJ) that connects to a power entry module
(KM01.1105.11, Schurter Inc., Santa Rosa, CA) which can be powered to a
standard AC 110V wall outlet. The power supply is connected to a custom
power distribution board responsible for powering the internal
components of the Control Center. The internal components powered by the
power distribution board include the three SBC compression units, the
ethernet switch, a fan (MF40100V1-1000U-A99, Sunon Fans, Brea, CA) and a
microcontroller (2590, Adafruit Industries LLC, New York, NY). The fan
helps with thermal management by providing airflow through the Control
Center to prevent overheating of the internal components. The
microcontroller allows for controlling auxiliary power options. The
Control Center has multiple connections in the rear as shown in figure
2. Two connections are for the power module and ethernet port. Three
connections are for individual data communication between the Control
Center and each SAHM system. Three 6 pin connectors are available for
auxiliary power for future abilities such as controlling LED lighting on
each of the SAHM systems.

A picture containing electronics, camera Description automatically generated

Figure The Control Center backside with electrical connections and fan.

## System Fabrication 

The Control Center was designed using 3D computer-aided design (CAD)
software SolidWorks 2022 (Dassault Systems SolidWorks Corporation,
Concord, NH). ABS material components were printed using a FDM printer
(F370, Stratasys, Rehovot, Israel). Cast acrylic components were cut
from bulk material using a CO<sub>2</sub> laser cutter (PLS6.150D,
Universal Laser Systems, Scottsdale, AZ).

## Enclosure Fabrication

The enclosure consists of four parts: the main body, rail, top panel,
and right panel. The top and right panels were fabricated by cutting
them out of 12”x24”x1/8” cast acrylic using a laser cutter. Afterwards
countersinks were drilled into the holes using a 90° Countersink drill
bit. The main body and rail were 3D printed using a FDM 3D printer and
GrabCAD Print software from Stratasys. The print orientation for the
parts at 0.0130-inch slice height is shown in figure 10.

A picture containing electronics Description automatically generated

Figure Main body and rail orientation for 3D printing in GrabCAD Print.

## Control Center Assembly

The bill of materials for the assembly of the Control Center is shown in
Table 2. The main body, rail, top panel, and side panel must be
fabricated as previously mentioned. The power distribution board must
also be fabricated. In this design, the power distribution board was
designed in Altium Designer (Altium, San Diego, CA) and fabricated using
a circuit board plotter (LPKF S104, LPKF Laser & Electronics, Garbsen,
Germany). Items that were custom made have .DXF or .STL files to
reference on the Github page. The other items were purchased from
vendors.

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

Bill of materials for the Control Center assembly.

### Side and Top Panel Assemblies

To allow for assembly of the internal components of the Control Center,
there needs to be access from the user to get inside the enclosure. The
user can do this by removing the side and top panels of the Control
Center. Each panel will have its own subassembly to allow for easy
removal and installation of each panel. The side panel requires the 3D
printed rail, three M3, 8mm pan screws, three cube standoffs, and three
M3, 8mm flat screws. The instructions for the side panel assembly are
shown in Figure 11.



Figure The side panel subassembly.

The top panel requires five M3, 8mm flat screws and five cube standoffs.
The top panel assembly is shown in Figure 12.



Figure The top panel subassembly.

### Electronic Subassemblies

The electronic subassemblies should be assembled before inserting into
the enclosure. The subassemblies will be for the power supply, power
distribution board, and the SBC units. The power supply and power
distribution board assembly each require four M3, 8mm pan screws and
four M3, 8mm standoffs female/female. The power supply and the power
distribution board instructions are shown in Figures 13 and 14.



Figure The power supply subassembly.



Figure The power distribution board subassembly.

To consolidate space, the three SBC compression units are stacked on one
another using standoffs. To do this, an SBC subassembly must be made.
The subassembly requires eight M3, 35mm standoffs male/female, four M3,
6mm standoffs male/female, and four M3 nuts. All parts can be hand
tightened. The instructions for the SBC subassembly are shown in Figure
15.



Figure Compression unit subassembly.

### Main Body Assembly

The next steps involve inserting the subassemblies and other components
into the main body. The first six steps of this process are shown in
figure 16. A No. 2 Phillips screwdriver will be required for these
steps. These steps involve installing all the electronic subassemblies
(SBC, power distribution board, and power supply) plus the switch and
USB mount.



Figure Steps 1 to 6 of the enclosure assembly.

The next steps will include assembling the fan and wiring for it. A 3
pin plug can be attached to the fan wire to plug into the power
distribution board. There are loops available to organize wires inside
the enclosure. The power mount and ethernet mount will also be assembled
during these steps. The power mount will require a 2 pin plug to be
attached and connected to the power supply. For the 2 pin plug, a hand
crimper (0640160205, Molex, Lisle, IL), pins, and 20 gauge wire will be
needed. Three M12 connectors will also be added and held in place with
locknuts. These steps are shown in Figure 17.



Figure Steps 7 to 12 of the enclosure assembly.

Step 13 involves wiring the 6 pin connectors to the assigned terminal on
the power distribution board. Steps 14 and 15 are for mounting two
standoff cubes. Step 16 will require a custom cable made from two 14 pin
plugs. The cable will need to have 28 pins, two 14 pin plugs, 20 gauge
wire, and require the Molex hand crimper. Step 17 connects the three SBC
units to the power distribution board using USB A to C cables. Step 18
connects the three SBC units to the switch via 2ft ethernet cables.
Steps 13 to 18 are shown in Figure 18.



Figure Steps 13 to 18 of the enclosure assembly.

Step 19 will connect the ethernet mount to the switch via a 1ft cable. A
custom cable with two 3 pin plugs connects the power distribution board
to the switch. The cable will have 6 pins, two 3 pin plugs, 20 gauge
wire and require the Molex crimper. Now all connections inside the
Control Center are complete and it is operational. The last two steps
will be to install the side panel and top panel subassemblies to finish
the enclosure. These steps are shown in figure 19. The finished assembly
of the Control Center is shown in Figure 20.



Figure Steps 19 to 22 of the enclosure assembly.



Figure Finished Control Center assembly.

# Modular Rack Assembly

## Modular Rack Overview

The modular rack is responsible for securing the three SAHM units and
control center in place for testing. The rack is non ventilated and is
designed to be used in a high density format. The modular rack setup
will allow for easy removal of SAHM units for repairs, maintenance,
animal care, etc.

## Modular Rack Fabrication

To assemble the modular rack, several parts will need to be custom
fabricated. Three Runner Support Bars (8975K582, McMaster-Carr,
Elmhurst, IL) will need to be machined. Two Igloo Bars (8975K582,
McMaster-Carr, Elmhurst, IL) will also need to be machined. In this
fabrication process, a waterjet was used to fabricate the bars. Two
runner bar brackets will need to be 3D printed. In this fabrication
process, the Markforged X7 (Waltham, MA) was used to print the parts out
of Onyx.

## Modular Rack Assembly

The bill of materials for the assembly of the Modular Rack is shown in
Table 3. Items that were custom made have .STL files to reference on the
Github page. The other items were purchased from vendors.

<table>
<caption><p>Bill of materials for the Modular Rack
assembly.</p></caption>
<colgroup>
<col style="width: 7%" />
<col style="width: 15%" />
<col style="width: 22%" />
<col style="width: 14%" />
<col style="width: 17%" />
<col style="width: 8%" />
<col style="width: 14%" />
</colgroup>
<thead>
<tr class="header">
<th>ITEM NO.</th>
<th>Part Label</th>
<th>Description</th>
<th>Source</th>
<th>Vendor Part Number</th>
<th>Qty</th>
<th>Cost</th>
</tr>
</thead>
<tbody>
<tr class="odd">
<td>1</td>
<td>Cage Runner</td>
<td>NIEHS CAN K10000 Kit, Runners, NexGen, Left/Right, Hardware, Glass
Filled Polysulfone High Temperature Plastic, Purple</td>
<td>Allentown Inc.</td>
<td>K10000</td>
<td>4</td>
<td>$216.00</td>
</tr>
<tr class="even">
<td>2</td>
<td>Cross Bar</td>
<td>1 x 1 x 16.5 inches T-Slotted profile - Four Open T-slots</td>
<td>80/20</td>
<td>8020-1010-black x 16.5</td>
<td>10</td>
<td>$167.90</td>
</tr>
<tr class="odd">
<td>3</td>
<td>Side Bar</td>
<td>1 x 1 x 15.5 inches T-Slotted profile - Four Open T-slots</td>
<td>80/20</td>
<td>8020-1010-black x 15.5</td>
<td>6</td>
<td>$97.62</td>
</tr>
<tr class="even">
<td>4</td>
<td>Vertical Bar</td>
<td>1 x 1 x 30 inches T-Slotted profile - Four Open T-slots</td>
<td>80/20</td>
<td>8020-1010-black x 30</td>
<td>4</td>
<td>$55.24</td>
</tr>
<tr class="odd">
<td>5</td>
<td>Corner Bracket</td>
<td>10 Series 2 Hole - Gusseted Inside Corner Bracket</td>
<td>80/20</td>
<td>8020-4132-black</td>
<td>16</td>
<td>$130.88</td>
</tr>
<tr class="even">
<td>6</td>
<td>1/4"-20, 1/2" Pan</td>
<td>1/4-20 x .500" Button Head Socket Cap Screw (BHSCS)</td>
<td>80/20</td>
<td>8020-3061</td>
<td>38</td>
<td>$12.92</td>
</tr>
<tr class="odd">
<td>7</td>
<td>1/4"-20 T-Nut</td>
<td>1/4-20 Roll-In T-Nut with Ball Spring</td>
<td>80/20</td>
<td>8020-3923</td>
<td>42</td>
<td>$102.48</td>
</tr>
<tr class="even">
<td>8</td>
<td>Igloo Bar</td>
<td>24" x 2" x 1/8" (L x W x H) metal bar</td>
<td>McMaster-Carr</td>
<td>8975K582</td>
<td>2</td>
<td>$14.10</td>
</tr>
<tr class="odd">
<td>9</td>
<td>Locking Clamp</td>
<td>10 Series 90 Degree Structural Right Angle Pivot Nub</td>
<td>80/20</td>
<td>8020-4002-black</td>
<td>4</td>
<td>$44.00</td>
</tr>
<tr class="even">
<td>10</td>
<td>Corner Connector</td>
<td>10 series 3-Way Square Corner Connector</td>
<td>80/20</td>
<td>8020-4042-Black</td>
<td>8</td>
<td>$265.84</td>
</tr>
<tr class="odd">
<td>11</td>
<td>1/4"-20, 1" Pan</td>
<td>1/4-20 x 1.000" Low Head Socket Cap Screw (LHSCS)</td>
<td>80/20</td>
<td>8020-3017</td>
<td>24</td>
<td>$18.72</td>
</tr>
<tr class="even">
<td>12</td>
<td>M4 T-Nut</td>
<td>M4 roll-in T-nut with ball spring</td>
<td>80/20</td>
<td>8020-3919</td>
<td>16</td>
<td>$39.04</td>
</tr>
<tr class="odd">
<td>13</td>
<td>M4, 10mm Pan</td>
<td>Black-Oxide Alloy Steel Socket Head Screw M4 x 0.7 mm Thread, 10 mm
Long</td>
<td>McMaster-Carr</td>
<td>91290A144</td>
<td>16</td>
<td>$1.80</td>
</tr>
<tr class="even">
<td>14</td>
<td>Runner Support Bar</td>
<td>36" x 2" x 1/8" (L x W x H) metal bar</td>
<td>McMaster-Carr</td>
<td>8975K582</td>
<td>3</td>
<td>$29.40</td>
</tr>
<tr class="odd">
<td>15</td>
<td>1/4"-20 Washer</td>
<td>Zinc Yellow-Chromate Plated Steel Oversized Washer
Grade 8, for 1/4" Screw Size, 0.281" ID, 0.625" OD</td>
<td>McMaster-Carr</td>
<td>98025A029</td>
<td>1</td>
<td>$0.20</td>
</tr>
<tr class="even">
<td>16</td>
<td>Runner Bar Bracket</td>
<td>3D Printed FDM</td>
<td>3D printed</td>
<td>N/A - refer to STL file</td>
<td>2</td>
<td>$8.00</td>
</tr>
<tr class="odd">
<td>17</td>
<td>1/4"-20, 3/4" Flat</td>
<td>82 Degree Countersink, 1/4"-20 Thread, 3/4" Long, Undercut</td>
<td>McMaster-Carr</td>
<td>96640A286</td>
<td>1</td>
<td>$14.37</td>
</tr>
<tr class="even">
<td colspan="6">Total Cost Per Modular Rack</td>
<td>$1,218.51</td>
</tr>
</tbody>
</table>

Bill of materials for the Modular Rack assembly.

#### Rack Top Subassembly

To make the assembly of the modular rack more user friendly, it is best
to assemble subassemblies of the rack. There are three subassemblies:
the rack top, base, mid bar, and rear bar. They can be completed in any
order. For the modular rack, one top subassembly is required. A 1/8”,
5/32”, and 3/16” Allen key are required for assembly. First the runner
bar bracket will be secured to a cross bar 195mm from the edge of the
crossbar. Second, two corner brackets will be secured to the opposite
side of the cross bar. Next two side bars will slide onto each face end
of the cross bar. Secure the cross bar 312mm offset from one end of the
side bar. Please refer to Figure 21 for steps 1 to 4 of the rack top
subassembly.



Figure Steps 1 to 4 of the rack top subassembly.

Two ¼”-20 T-Nuts will slide into the inner rails of the side bars. Do
not secure these T-nuts, they will be secured in a later step. Next
slide two T-nuts (a part of the Locking Clamp assembly, P/N
8020-4002-black, Allentown Inc., Allentown, NJ) and an Igloo bar on the
inside rails of the side bars. Secure the igloo bar in place
approximately 78mm offset from the side bar face end. The igloo bar is
secured by the rest of the Locking Clamp (P/N 8020-4002-black, Allentown
Inc., Allentown, NJ). Next fasten two corner brackets onto each face end
of two new cross bars. Please refer to Figure 22 for steps 5 to 8 of the
rack top subassembly.



Figure Steps 5 to 8 of the rack top subassembly.

The final step involves fastening the cross bars with the corner
connectors to the face ends of the side bars. The final step and
resulting rack top subassembly can be found in Figure 23.



Figure Step 9 and finished version of the rack top subassembly.

#### Rack Base Subassembly

For the modular rack, one base subassembly is required. A 1/8” and 5/32”
Allen key are required for assembly. First the runner bar bracket will
be secured to a cross bar 195mm from the edge of the crossbar. Second,
two corner brackets will be secured to the opposite side of the cross
bar. Next two side bars will slide onto each face end of the cross bar.
Secure the cross bar 312mm offset from one end of the side bar. Please
refer to Figure 24 for steps 1 to 4 of the rack base subassembly.



Figure Figure 20 Steps 1 to 4 of the rack base subassembly.

Two ¼”-20 T-Nuts will slide into the inner rails of the side bars. Do
not secure these T-nuts, they will be secured in a later step. Next
fasten two corner brackets onto each face end of two new cross bars. The
final step involves fastening the cross bars with the corner connectors
to the face ends of the side bars. The final steps 5 to 9 and resulting
rack base subassembly can be found in Figure 25.



Figure Steps 5 to 7 and the finished version of the rack base
subassembly.

#### Rack Mid Bar Subassembly

For the modular rack, one mid bar subassembly is required. A 5/32” and
3/16” Allen key are required for assembly. First slide two T-nuts (a
part of the Locking Clamp assembly, P/N 8020-4002-black, Allentown Inc.,
Allentown, NJ) and an Igloo bar on the inside rails of the side bars.
Secure the igloo bar in place approximately 78mm offset from the side
bar face end. The igloo bar is secured by the rest of the Locking Clamp
(P/N 8020-4002-black, Allentown Inc., Allentown, NJ). Next on the bottom
side of the side bars, secure four corner brackets flesh to the face
ends of the side bars. The assembly steps 1 to 3 and resulting rack mid
bar subassembly can be found in Figure 26.



Figure Assembly steps and the finished version of the rack mid bar
subassembly.

#### Rack Rear Bar Subassembly

Four mid bar subassemblies are required for one modular rack. A 5/32”
Allen key is required for assembly. On the top side of the cross bar,
secure two corner brackets flesh to the face ends of the cross bars.
Next slide four M4 T-Nuts onto the front rail of the cross bar. Do not
secure these t-nuts yet. The assembly steps and resulting rack rear bar
subassembly can be found in Figure 27. Repeat these steps to make four
mid bar subassemblies in total.



Figure Assembly steps and the finished version of the rack rear bar
subassembly.

#### Rack Assembly 

Once all the subassemblies are completed for the modular rack, then the
final rack can be assembled. A 1/8”, 5/32”, and 3mm Allen key and a No.
2 Phillips screwdriver are required for assembly. First fasten the four
vertical bars to the base subassembly. Second, install the mid bar
subassembly and fasten it 350mm above the base subassembly. Next install
one rear bar subassembly between the two rear vertical posts. Make sure
the corner brackets are on the bottom side of the rear bar subassembly
and they are touching the base subassembly. Please refer to Figure 28
for steps 1 to 4 of the rack assembly.



Figure Steps 1 to 4 of the rack assembly.

The next step is to install the second rear bar sub assembly between the
two rear vertical posts. Make sure the corner brackets are on the top
side of the rear bar subassembly. Leave a 78mm gap between the first and
second rear cross bars. Please refer to Figure 29 for steps 5 to 8 of
the rack assembly.



Figure Steps 5 to 8 of the rack assembly.

A third rear bar sub assembly will need to be installed between the two
rear vertical posts. Make sure the corner brackets are on the bottom
side of the rear bar subassembly. Leave a 260mm gap between the second
and third rear cross bars. The final rear bar sub assembly will need to
be installed between the two rear vertical posts. Make sure the corner
brackets are on the top side of the rear bar subassembly. Leave a 78 mm
gap between the third and final rear cross bars. Next fasten the top sub
assembly to the top faces of the four vertical bars. Please refer to
Figure 30 for steps 9 to 12 of the rack assembly.



Figure Steps 9 to 12 of the rack assembly.

Next fasten one runner support to the left side bar on both the top and
base subassemblies. Make sure the runner support bar is square with the
two cross bars on both the top and base subassemblies. Slide another
runner support bar in between the two runner bar brackets and secure
with ¼”-20, ¾” flat screws. Fasten the last runner support to the right
side bar on both the top and base subassemblies. Make sure the runner
support bar is square with the two cross bars on both the top and base
subassemblies. Next install a left and right cage runner. Make sure the
dimples on the runners match with the cutouts on the runner support
bars. The cage runners will be fastened to the M4 T-Nuts in the two
lower rear bar subassemblies. Please refer to Figure 31 for steps 13 to
16 of the rack assembly.



Figure Steps 13 to 16 of the rack assembly.

Three more sets of a left and right cage runners will need to be
installed. Make sure the dimples on the runners match with the cutouts
on the runner support bars. The cage runners will be fastened to the M4
T-Nuts in the rear bar subassemblies. Please refer to Figure 32 for
steps 17 to 19 and the finished version of the rack assembly.



Figure Assembly steps 17 to 19 and the finished version of the modular
rack assembly.

# Appendix – Step by Step Instructions

## SAHM Assembly

### Hopper Assembly

Diagram, engineering drawing Description automatically generated

Diagram, engineering drawing Description automatically generated

Diagram, engineering drawing Description automatically generated

Diagram, engineering drawing Description automatically generated

### Igloo Assembly 

Chart, radar chart Description automatically generated

Diagram, engineering drawing Description automatically generated

Diagram, engineering drawing Description automatically generated

Diagram, engineering drawing Description automatically generated

Diagram, engineering drawing Description automatically generated

Diagram, engineering drawing Description automatically generated

Diagram Description automatically generated

Diagram, engineering drawing Description automatically generated

Engineering drawing Description automatically generated

### SAHM Unit Assembly

Diagram, engineering drawing Description automatically generatedDiagram, engineering drawing Description automatically generatedDiagram, engineering drawing Description automatically generatedA picture containing text, scale, device Description automatically generatedEngineering drawing Description automatically generated

## Control Center 

<span id="_Toc144982149" class="anchor"></span>Side Panel Subassembly

A picture containing text, hinge, metalware Description automatically generatedEngineering drawing Description automatically generated

Arrow Description automatically generatedDiagram Description automatically generatedArrow Description automatically generated

### Top Panel Subassembly

Chart, schematic Description automatically generatedA picture containing accessory, table, worktable Description automatically generated

### Power Supply Subassembly

Diagram Description automatically generated



### Power Distribution Board Subassembly

Diagram Description automatically generated

A picture containing text, electronics, circuit Description automatically generated

### SBC Subassembly

Diagram, engineering drawing Description automatically generatedDiagram, engineering drawing Description automatically generated

Diagram, engineering drawing Description automatically generatedDiagram, engineering drawing Description automatically generated
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

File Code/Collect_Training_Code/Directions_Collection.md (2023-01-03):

# Directions For Collecting Training frames

Run the following command in this directory:
```
make clean && make -j4
```

Then run 
```
./run_record.sh
```

# For decompressing the frames to images run the following
```
./run_decompress.sh
```

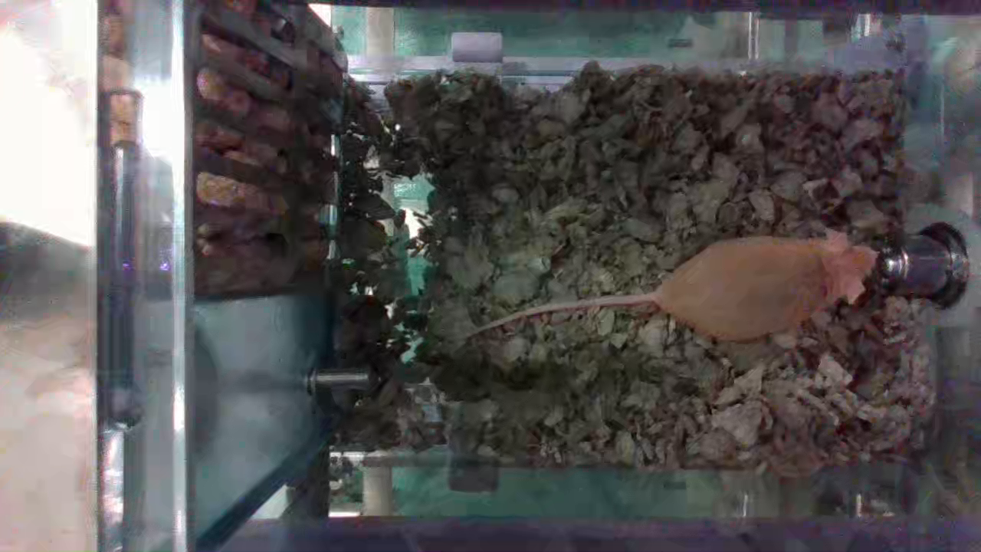
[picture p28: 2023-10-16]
Manuscript_Data/TanMouseAnnotations/images/color_2023-01-09 15_41_38.367807.png

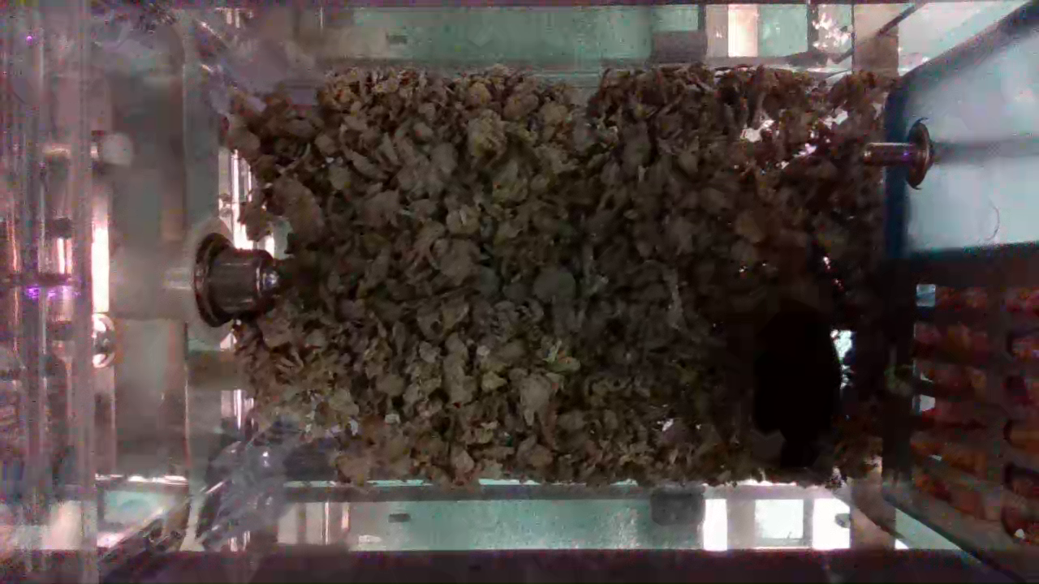
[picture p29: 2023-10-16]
Manuscript_Data/BlackMouseAnntoations/images/color_2023-01-06 15_07_28.259553.png

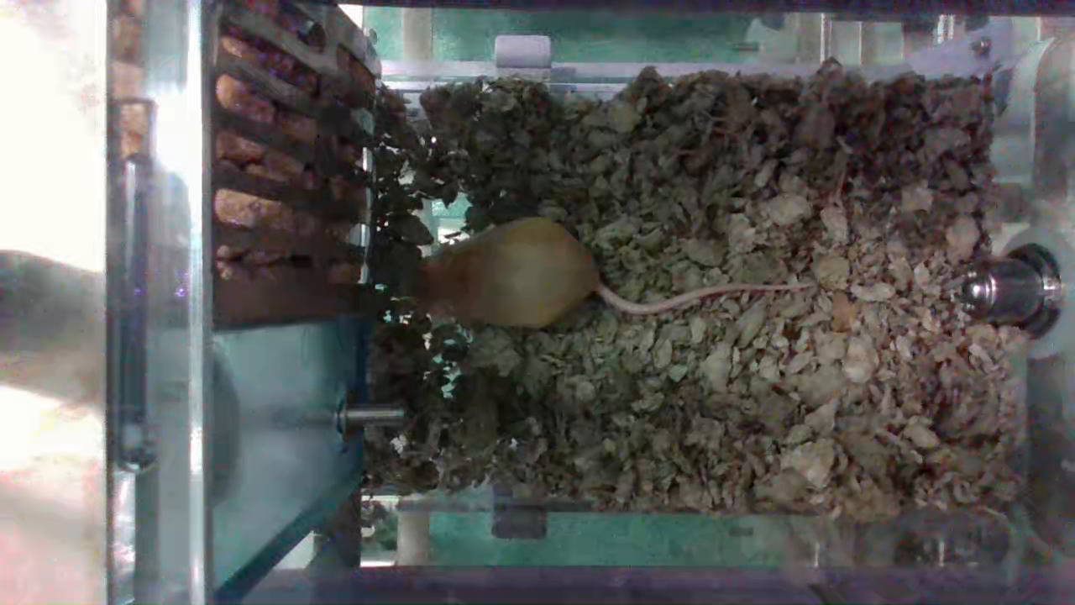
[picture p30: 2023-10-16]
Manuscript_Data/TanMouseAnnotations/images/color_2023-01-09 16_15_38.959435.png

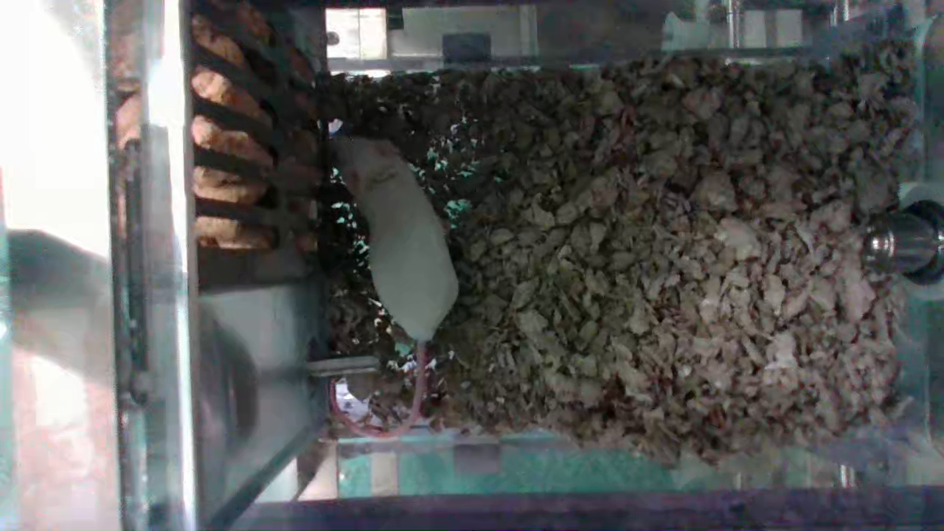
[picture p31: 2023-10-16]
Manuscript_Data/WhiteMouseAnnotations/images/color_2023-01-10 18_05_17.452792.png

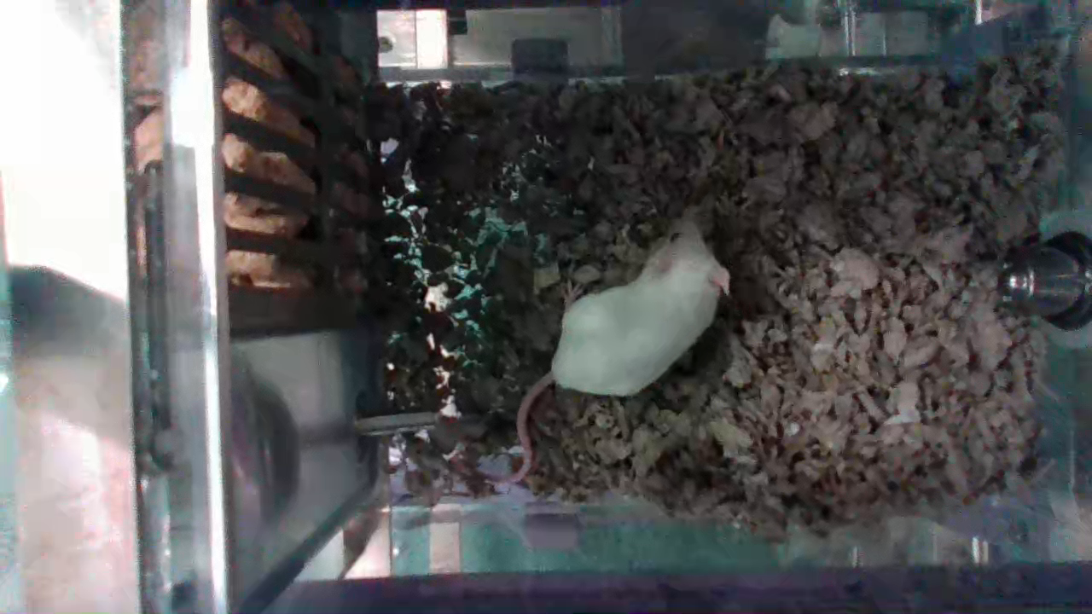
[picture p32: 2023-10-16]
Manuscript_Data/WhiteMouseAnnotations/images/color_2023-01-10 16_33_25.100010.png

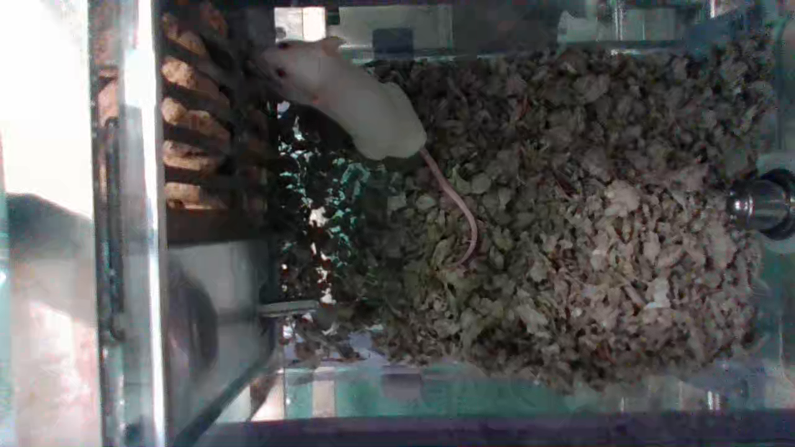
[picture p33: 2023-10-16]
Manuscript_Data/WhiteMouseAnnotations/images/color_2023-01-10 16_34_25.963991.png

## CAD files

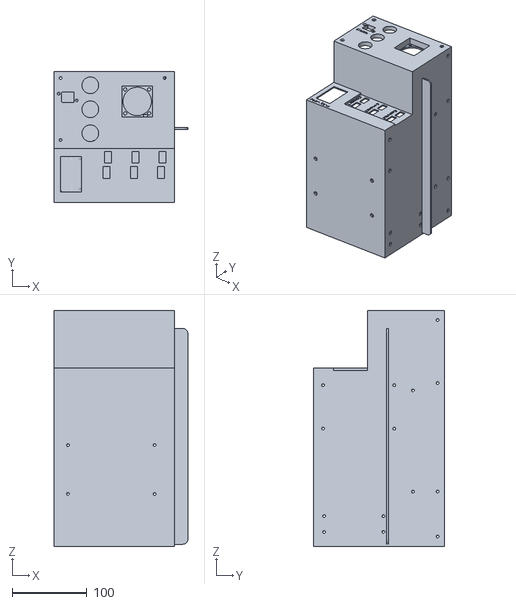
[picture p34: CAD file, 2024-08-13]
CAD_Models/SCHORE_Allentown_Full_CAD_files/Main Body.STL
178.8 x 175.0 x 315.0

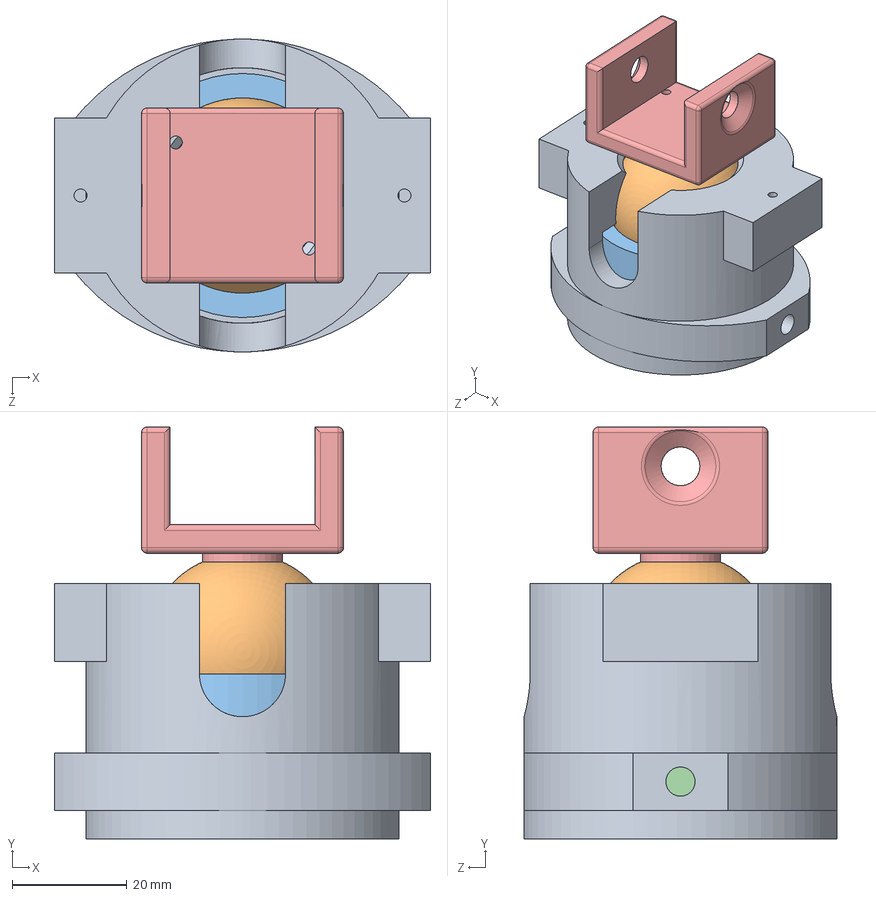
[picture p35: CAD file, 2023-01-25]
CAD_Models/SCHORE_Allentown_Full_CAD_files/ballSocket_cameraHolder.SLDASM
65.5 x 71.8 x 54.5 mm
external case
35mm ball
bearing cup
friction pad x 2
intelCamera_bracket

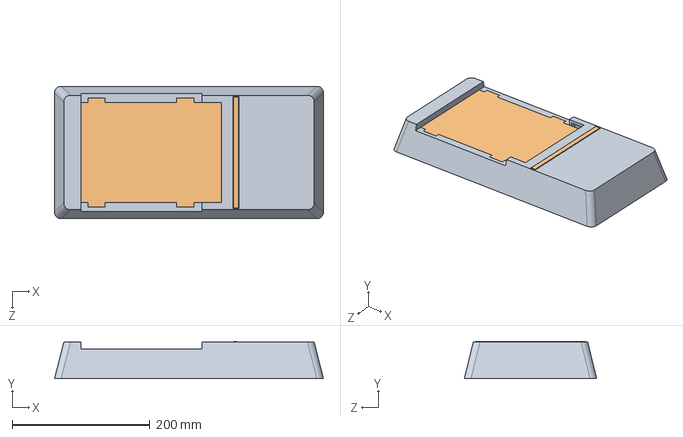
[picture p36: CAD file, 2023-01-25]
CAD_Models/SCHORE_Allentown_Full_CAD_files/allentown_igloo.SLDASM
390.0 x 53.9 x 192.0 mm
allentown_lid_forCutout
allentown_lidcutout

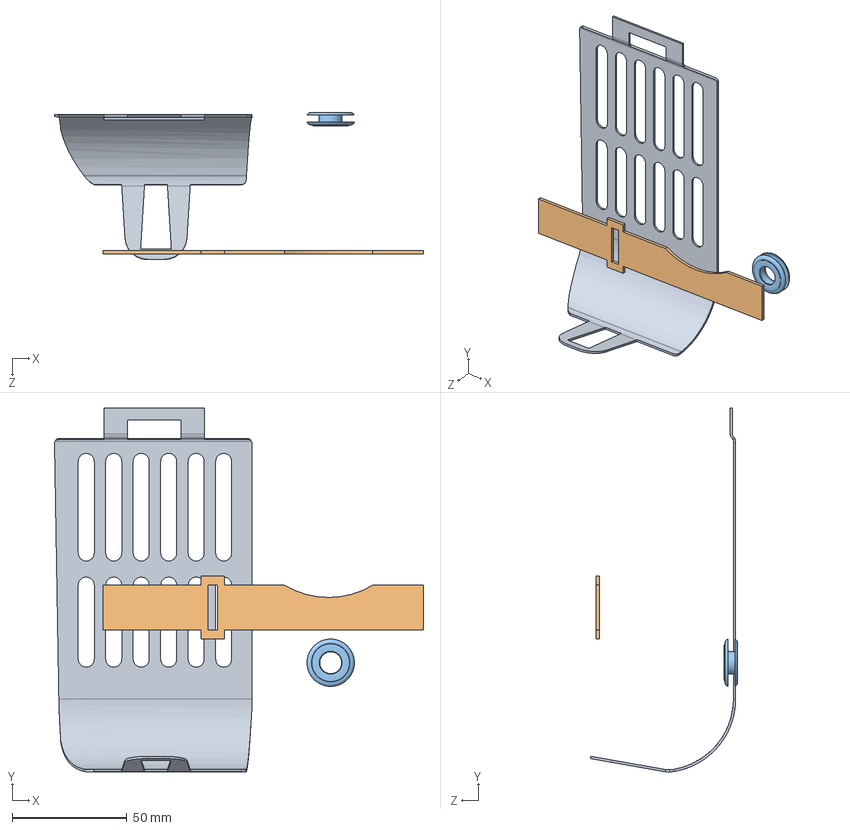
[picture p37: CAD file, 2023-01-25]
CAD_Models/SCHORE_Allentown_Full_CAD_files/Hopper3.2.SLDASM
161.1 x 158.8 x 64.3 mm
Grate32
Branch
96015K33_Stainless Steel Fabric Grommets with Washer

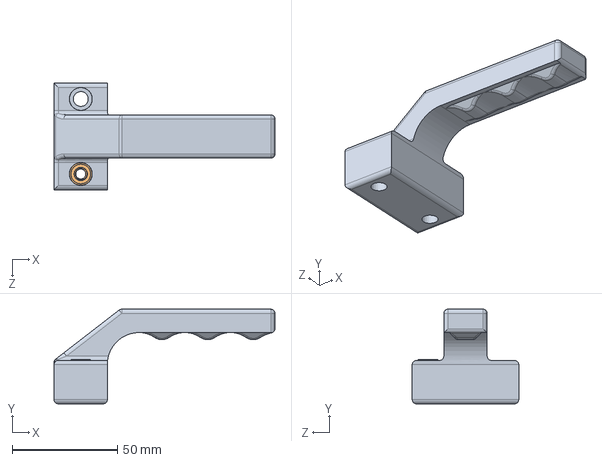
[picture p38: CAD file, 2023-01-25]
CAD_Models/SCHORE_Allentown_Full_CAD_files/handleModified.SLDASM
105.0 x 45.0 x 50.6 mm

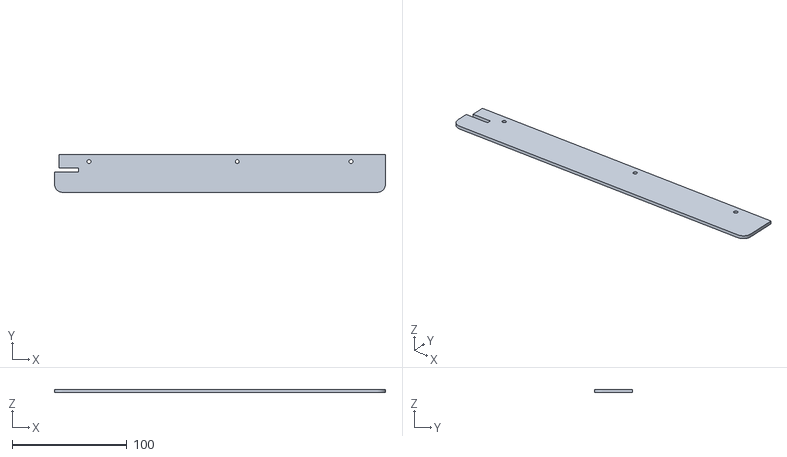
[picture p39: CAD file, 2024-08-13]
CAD_Models/SCHORE_Allentown_Full_CAD_files/Rail.STL
288.0 x 32.8 x 2.60

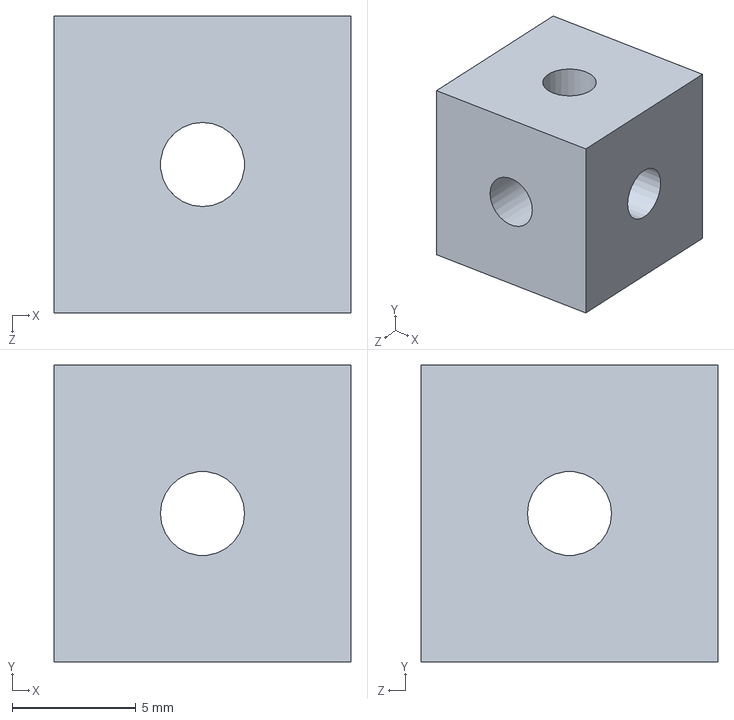
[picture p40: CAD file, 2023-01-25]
CAD_Models/SCHORE_Allentown_Full_CAD_files/Cube Standoff.SLDPRT
12.0 x 12.0 x 12.0 mm

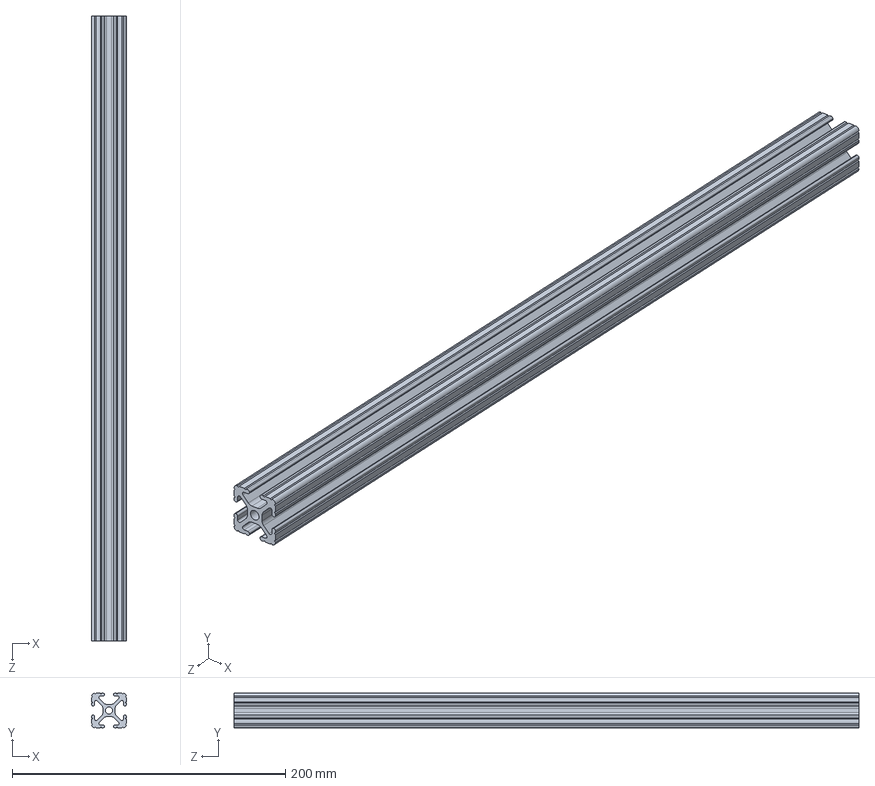
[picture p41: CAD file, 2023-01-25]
CAD_Models/SCHORE_Allentown_Full_CAD_files/8020-1010-1010 X 48.SLDPRT
25.4 x 25.4 x 457.2 mm

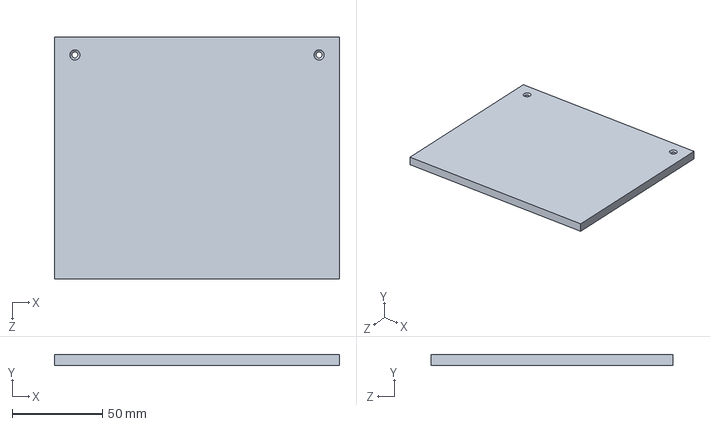
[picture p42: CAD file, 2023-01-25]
CAD_Models/SCHORE_Allentown_Full_CAD_files/allentown_igloo_rear.SLDPRT
158.0 x 6.30 x 134.2 mm

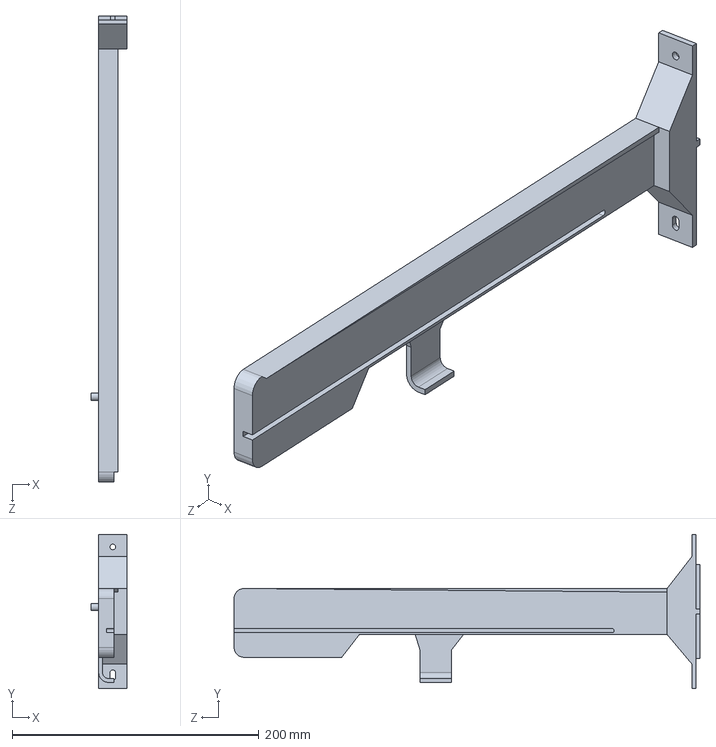
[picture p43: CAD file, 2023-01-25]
CAD_Models/SCHORE_Allentown_Full_CAD_files/Arm_rightSide.SLDPRT
29.3 x 125.2 x 377.8 mm

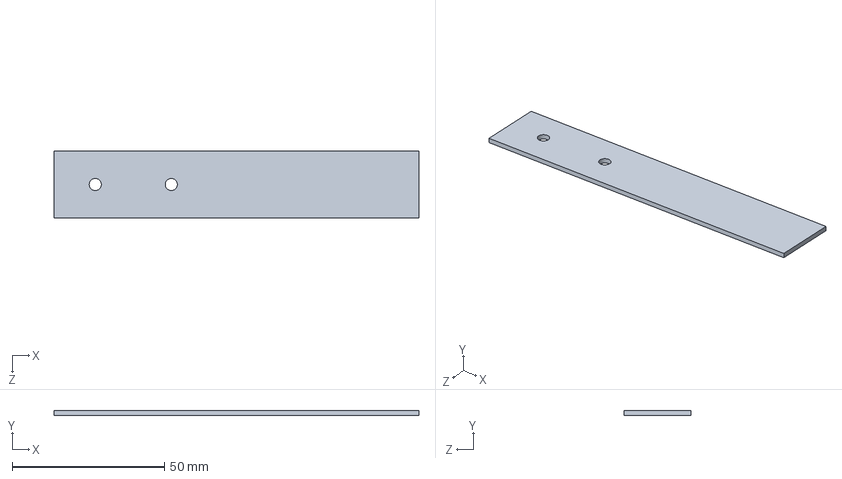
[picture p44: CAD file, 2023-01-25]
CAD_Models/SCHORE_Allentown_Full_CAD_files/Branch.SLDPRT
120.0 x 1.59 x 22.0 mm

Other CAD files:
CAD_Models/SCHORE_Allentown_Full_CAD_files/2310.sldasm
CAD_Models/SCHORE_Allentown_Full_CAD_files/4002.sldasm
CAD_Models/SCHORE_Allentown_Full_CAD_files/Side Panel.DWG
CAD_Models/SCHORE_Allentown_Full_CAD_files/Top Panel.DWG
CAD_Models/SCHORE_Allentown_Full_CAD_files/4002_5.sldprt
CAD_Models/SCHORE_Allentown_Full_CAD_files/4132.sldprt
CAD_Models/SCHORE_Allentown_Full_CAD_files/2310_7.sldprt
CAD_Models/SCHORE_Allentown_Full_CAD_files/1010_15_5_CL.sldprt
CAD_Models/SCHORE_Allentown_Full_CAD_files/13027_m.sldprt
CAD_Models/SCHORE_Allentown_Full_CAD_files/13037_m.sldprt
CAD_Models/SCHORE_Allentown_Full_CAD_files/2143.sldprt
CAD_Models/SCHORE_Allentown_Full_CAD_files/2310_3.sldprt
CAD_Models/SCHORE_Allentown_Full_CAD_files/2310_5.sldprt
CAD_Models/SCHORE_Allentown_Full_CAD_files/3061.sldprt
CAD_Models/SCHORE_Allentown_Full_CAD_files/4002_3.sldprt
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

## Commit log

2022-07-13 Looping through blocks and filtering out noise in black parts of image
2022-07-17 Playing with B frames
2022-07-17 Playing with B frames 3
2022-07-17 Playing with B frames 4 no bframes
2022-07-17 Playing with B frames making a compression ratio comparison chart
2022-07-27 Minor edits fixed segfault
    [dcomp_Depth_metadata.csv, other_Depth_metadata.csv]
2022-07-27 Apparently two 8 bit frames better?
2022-12-27 Fixed some issues with seeing cameras
2022-12-30 Added infared functionality to collect training frames
2023-01-03 Made edits to extracting frames
2023-01-06 Fixed some threading issues aligning frames
2023-01-06 Fixed more for aligning frames
2023-01-25 Added CAD files
    [1010_15_5_CL.sldprt, 13027_m.sldprt, 13037_m.sldprt, 2143.sldprt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]
2023-04-14 Added OKS data
    [25AgoudiColorDLC_resnet50_wbargbJan25shuffle1_182000_oks.csv, 25AgoudiDepthDLC_resnet50_wbaJan24shuffle1_182000_oks.csv, 25BlackColorDLC_resnet50_wbargbJan25sh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]
2023-09-07 Added Assembly_Instructions in Models folder deleted unused folders
2023-09-07 Renamed something
    [1010_15_5_CL.sldprt, 13027_m.sldprt, 13037_m.sldprt, 2143.sldprt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]
2023-09-07 Added where assembly instructions can be found
2023-10-16 Changed name of directory
    [25AgoudiColorDLC_resnet50_wbargbJan25shuffle1_182000_oks.csv, 25AgoudiDepthDLC_resnet50_wbaJan24shuffle1_182000_oks.csv, 25BlackColorDLC_resnet50_wbargbJan25sh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]
2023-10-16 4 more
    [25TanColorDLC_resnet50_wbargbJan25shuffle1_182000_oks.csv, 25TanDepthDLC_resnet50_wbaJan24shuffle1_182000_oks.csv]
2023-12-13 Update README.md
    replaced all references to 'igloo' with 'camera mounting enclosure'
2024-08-13 Add PCM design files
    [Main Body.STL, Rail.STL, Side Panel.DWG, Top Panel.DWG]
